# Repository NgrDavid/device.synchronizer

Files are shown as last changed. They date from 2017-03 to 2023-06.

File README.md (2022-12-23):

## Harp Synchronizer

Used to synchronize and align the different apparatus and devices present in a complex setup. It timestamps each rising or falling edge of the 9 digital input signals. The sampling of the inputs can also be configured to use a ﬁxed sampling frequency.

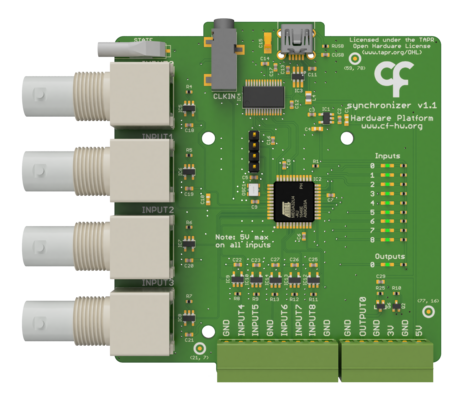
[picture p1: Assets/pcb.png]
harpsynchronizer


### Key Features ###

* Receives and timestamps up to 9 digital input signals
* Sampling on signal transitions or fixed sampling frequency up to 2kHz

### Connectivity ###

* 1x clock sync input (CLKIN) [stereo jack]
* 1x USB (for computer) [USB type B]
* 9x digital inputs (DIN0 to DIN5) [BNC], (DIN6 to DIN8) [screw terminal]
* 1x digital output (DOUT0) [screw terminal]

## Interface ##

The interface with the Harp board can be done through [Bonsai](https://bonsai-rx.org/) or a dedicated GUI (Graphical User Interface).

In order to use this GUI, there are some software that needs to be installed:

1 - Install the [drivers](https://bitbucket.org/fchampalimaud/downloads/downloads/UsbDriver-2.12.26.zip).

2 - Install the [runtime](https://bitbucket.org/fchampalimaud/downloads/downloads/Runtime-1.0.zip).

3 - Reboot the computer.

4 - Install the [GUI](https://bitbucket.org/fchampalimaud/downloads/downloads/Harp%20Synchronizer%20v1.2.0.zip).

## Licensing ##

Each subdirectory will contain a license or, possibly, a set of licenses if it involves both hardware and software.

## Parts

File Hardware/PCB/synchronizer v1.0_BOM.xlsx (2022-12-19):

Board | Part(s) | Quantity | Description | Distributor | Part. No.
 | IC1 | 1 | LDO 150mA 30V Ultra-Lo IQ Wd Input LDO Reg | Mouser | TPS70933DBVR
 | IC2 | 1 | IC MCU 8BIT 32KB FLASH 44TQFP | Mouser | 556-ATXMEGA32A4U-AU
 | IC3 | 1 | ESD Protection Low Cap | Mouser | 511-USBLC6-2SC6
 | IC4 | 1 | IC USB USB to Serial UART Enhanced IC SSOP-28 | Mouser | 895-FT232RL
 | IC5, IC6, IC7, IC8, IC9, IC10, IC12, IC13, IC14 | 9 | SingleBuffer / Driver, Inverting, 3-State, 1.65V to 5.5V, SOT-23-5 | Mouser | 595-SN74LVC1G240DBVT
 | IC11 | 1 | Buffers e line drivers 1.65-5.5V Single Non-Inverting TTL | Mouser | 863-M74VHC1GT50DTT1G
 | C12, C13 | 2 | CAP CER 47pF 50V C0G 5% 0402 | Mouser | 77-VJ0402A470JXACBC
 | CUSB | 1 | CAP CER 4.7nF 100V 10% X7R 0402 | Mouser | 81-GRM155R72A472KA01
 | C2, C5, C6, C7, C8, C11, C14, C16, C17, C18, C19, C20, C21, C22, C23, C24, C25, C26, C27 | 19 | CAP CER 100nF 10V X5R 0402 | REEL | REEL
 | C9 | 1 | CAP CER 0.33uF 10V 10% X5R 0402 | Mouser | GRM155R61A334KE15D
 | C15 | 1 | CAP TAN 4.7uF 6.3V 10% 1206 | Mouser | 80-T491A475K006
 | C4 | 1 | CAP CER 4.7uF 10V 10% X5R 0603 | Mouser | GRM188R61A475KE15D
 | C1, C10 | 2 | CAP CER 10uF 10V 10% X5R 0603 | Mouser | 81-GRM188R61A106KE9D
 | R24 | 1 | RES SMD 0Ω OHM 5% 0402 | Mouser | 71-CRCW0402-0-E3
 | R1, R14, R15, R16, R17, R18, R19, R20, R21, R22, R23 | 11 | RES SMD 68Ω OHM 5% 0402 | Mouser | 71-CRCW0402-68-E3
 | R3 | 1 | RES SMD 680Ω 0.5% 0402 | Mouser | 754-RR0510P-681D
 | R2 | 1 | RES SMD 2050Ω 1% 0402 | Mouser | 71-CRCW0402-2.05K-E3
 | R4, R5, R6, R7, R8, R9, R11, R12, R13 | 9 | RES SMD 100kΩ 1% 0402 | REEL | REEL
 | RUSB | 1 | RES SMD 1MΩ 1/4W 5% 75V 0603 | Mouser | 71-CRCW06031M00JNEAH
 | L4 | 1 | 40ohms 100MHz 1.5A Monolithic 0805 SMD | Mouser | 875-MI0805K400R-10
 | RX, STATE, OUT00, OUT01, OUT02, OUT03, OUT04, OUT05, OUT10, OUT11, OUT12, OUT13 | 12 | GREEN LED | Mouser | 78-TLMP1100-GS08
 | TX | 1 | RED LED | Mouser | 720-LSQ976-NR-1
 | OSC1 | 1 | 32MHz 10ppm | Mouser | 998-1001CI5032.0000T
 | PDI | 1 | 4POS HDR 30AU | Mouser | 649-68000-104HLF
 | A0, A1 | 2 | 3POS Gold Male | Mouser | 649-68001-203HLF
 |  | 1 | SHUNT JUMPER, 2POS | Farnell | 2396301
 | CTRL0.0, CTRL0.1, CTRL0.2, CTRL0.3, CTRL0.4, CTRL0.5 | 6 | R.A. JACK 50 OHM | Mouser | 571-5227161-1
 | X1 | 1 | TERMINAL BLOCK, HEADER, 8POS, TH | Farnell | 2517863
 |  | 1 | Pluggable Terminal Block, 8, 125 V, 12 A, 3.5 mm, 28 AWG, 16 AWG | Farnell | 2575220
 | USB | 1 | UX60-MB-5S8 | Mouser | 798-UX60-MB-5S8
 | USB Cable | 1 | USB A - MINI-B 0.8M - MINI-B 0.8M BLACK | Mouser | 538-88732-8502
 | CLKIN | 1 | SMT 3.5 STEREO REEL | Mouser | 502-35RASMT2BHNTRX
 | Standoff Top | 9 | Standoff, Nylon 6.6 (Polyamide 6.6), Hex Female, M3, 8 mm | Farnell | 1733419
 | Standoff Bottom | 9 | Standoff, Nylon 6.6 (Polyamide 6.6), Hex Male-Female, M3, 8 mm | Farnell | 1733427
 | Screws | 18 | Screw, M3, 6 mm, Nylon (Polyamide), Pan Head Slotted | Farnell | 1514409
 |  | 1 | Acrylics
 | Components | 132
 | Licensed under the TAPR Open Hardware License (www.tapr.org/OHL)
 | Copyright 2017 Artur Silva and Filipe Carvalho

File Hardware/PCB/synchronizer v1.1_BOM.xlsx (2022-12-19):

Part(s) | Quantity | Description | Distributor | Part. No.
IC1 | 1 | LDO 150mA 30V Ultra-Lo IQ Wd Input LDO Reg | Mouser | TPS70933DBVR
IC2 | 1 | IC MCU 8BIT 32KB FLASH 44TQFP | Mouser | 556-ATXMEGA32A4U-AU
IC3 | 1 | ESD Protection Low Cap | Mouser | 511-USBLC6-2SC6
IC4 | 1 | IC USB USB to Serial UART Enhanced IC SSOP-28 | Mouser | 895-FT232RL
IC5, IC6, IC7, IC8, IC9, IC10, IC12, IC13, IC14 | 9 | SingleBuffer / Driver, Inverting, 3-State, 1.65V to 5.5V, SOT-23-5 | Mouser | 595-SN74LVC1G240DBVT
C12, C13 | 2 | CAP CER 47pF 50V C0G 5% 0402 | Mouser | 77-VJ0402A470JXACBC
CUSB | 1 | CAP CER 4.7nF 100V 10% X7R 0402 | Mouser | 81-GRM155R72A472KA01
C2, C5, C6, C7, C8, C11, C14, C16, C17, C18, C19, C20, C21, C22, C23, C25, C26, C27 | 18 | CAP CER 100nF 25V X5R 0402
C3, C29 | 0 | NA | NA
C9 | 1 | CAP CER 0.33uF 10V 10% X5R 0402 | Mouser | GRM155R61A334KE15D
C15 | 1 | CAP TAN 4.7uF 6.3V 10% 1206 | Mouser | 80-T491A475K006
C4 | 1 | CAP CER 4.7uF 10V 10% X5R 0603 | Mouser | GRM188R61A475KE15D
C1, C10 | 2 | CAP CER 10uF 10V 10% X5R 0603 | Mouser | 81-GRM188R61A106KE9D
R1, R14, R15, R16, R17, R18, R19, R20, R21, R22, R23 | 11 | RES SMD 68Ω OHM 5% 0402 | Mouser | 71-CRCW0402-68-E3
R4, R5, R6, R7, R8, R9, R10, R11, R12, R13 | 10 | RES SMD 100kΩ 1% 0402
R25 | 1 | RES SMD 10kΩ 1% 0402
RUSB | 1 | RES SMD 1MΩ 1/4W 5% 75V 0603 | Mouser | 71-CRCW06031M00JNEAH
L4 | 1 | 40ohms 100MHz 1.5A Monolithic 0805 SMD | Mouser | 875-MI0805K400R-10
STATE, OUT00, OUT01, OUT02, OUT03, OUT04, OUT05, OUT10, OUT11, OUT12, OUT13 | 11 | GREEN LED | Mouser | 78-TLMP1100-GS08
Q2 | 1 |  | Farnell | 1843701
Q6 | 1 |  | Farnell | 1858672
OSC1 | 1 | 32MHz 10ppm | Mouser | 998-1001CI5032.0000T
PDI | 1 | 4POS HDR 30AU | Mouser | 649-68000-104HLF
IN0.0, IN0.1, IN0.2, IN0.3 | 4 | R.A. JACK 50 OHM | Mouser | 571-5227161-1
X1 | 1 | TERMINAL BLOCK, HEADER, 8POS, TH | Farnell | 2517863
 | 1 | Pluggable Terminal Block, 8, 125 V, 12 A, 3.5 mm, 28 AWG, 16 AWG | Farnell | 2575220
X2 | 1 | TERMINAL BLOCK, HEADER, 6POS, TH | Farnell | 2517862
 | 1 | Pluggable Terminal Block, 6, 125 V, 12 A, 3.5 mm, 28 AWG, 16 AWG | Farnell | 2575219
USB | 1 | UX60-MB-5S8 | Mouser | 798-UX60-MB-5S8
USB Cable | 1 | USB A - MINI-B 0.8M - MINI-B 0.8M BLACK | Mouser | 538-88732-8502
CLKIN | 1 | SMT 3.5 STEREO REEL | Mouser | 502-35RASMT2BHNTRX
NUT_M3_HEX_NYLON | 8 | Nut, Hex, M3, Nylon 6.6 | Farnell | 2472687
SCREW_M3_10MM_NYLON_PHILLIPS | 4 | Machine Screw, M3, 10 mm, Nylon (Polyamide), Pan Head Slotted | Farnell | 1514410
Components | 101
Licensed under the TAPR Open Hardware License (www.tapr.org/OHL)
Copyright 2017 Artur Silva and Filipe Carvalho

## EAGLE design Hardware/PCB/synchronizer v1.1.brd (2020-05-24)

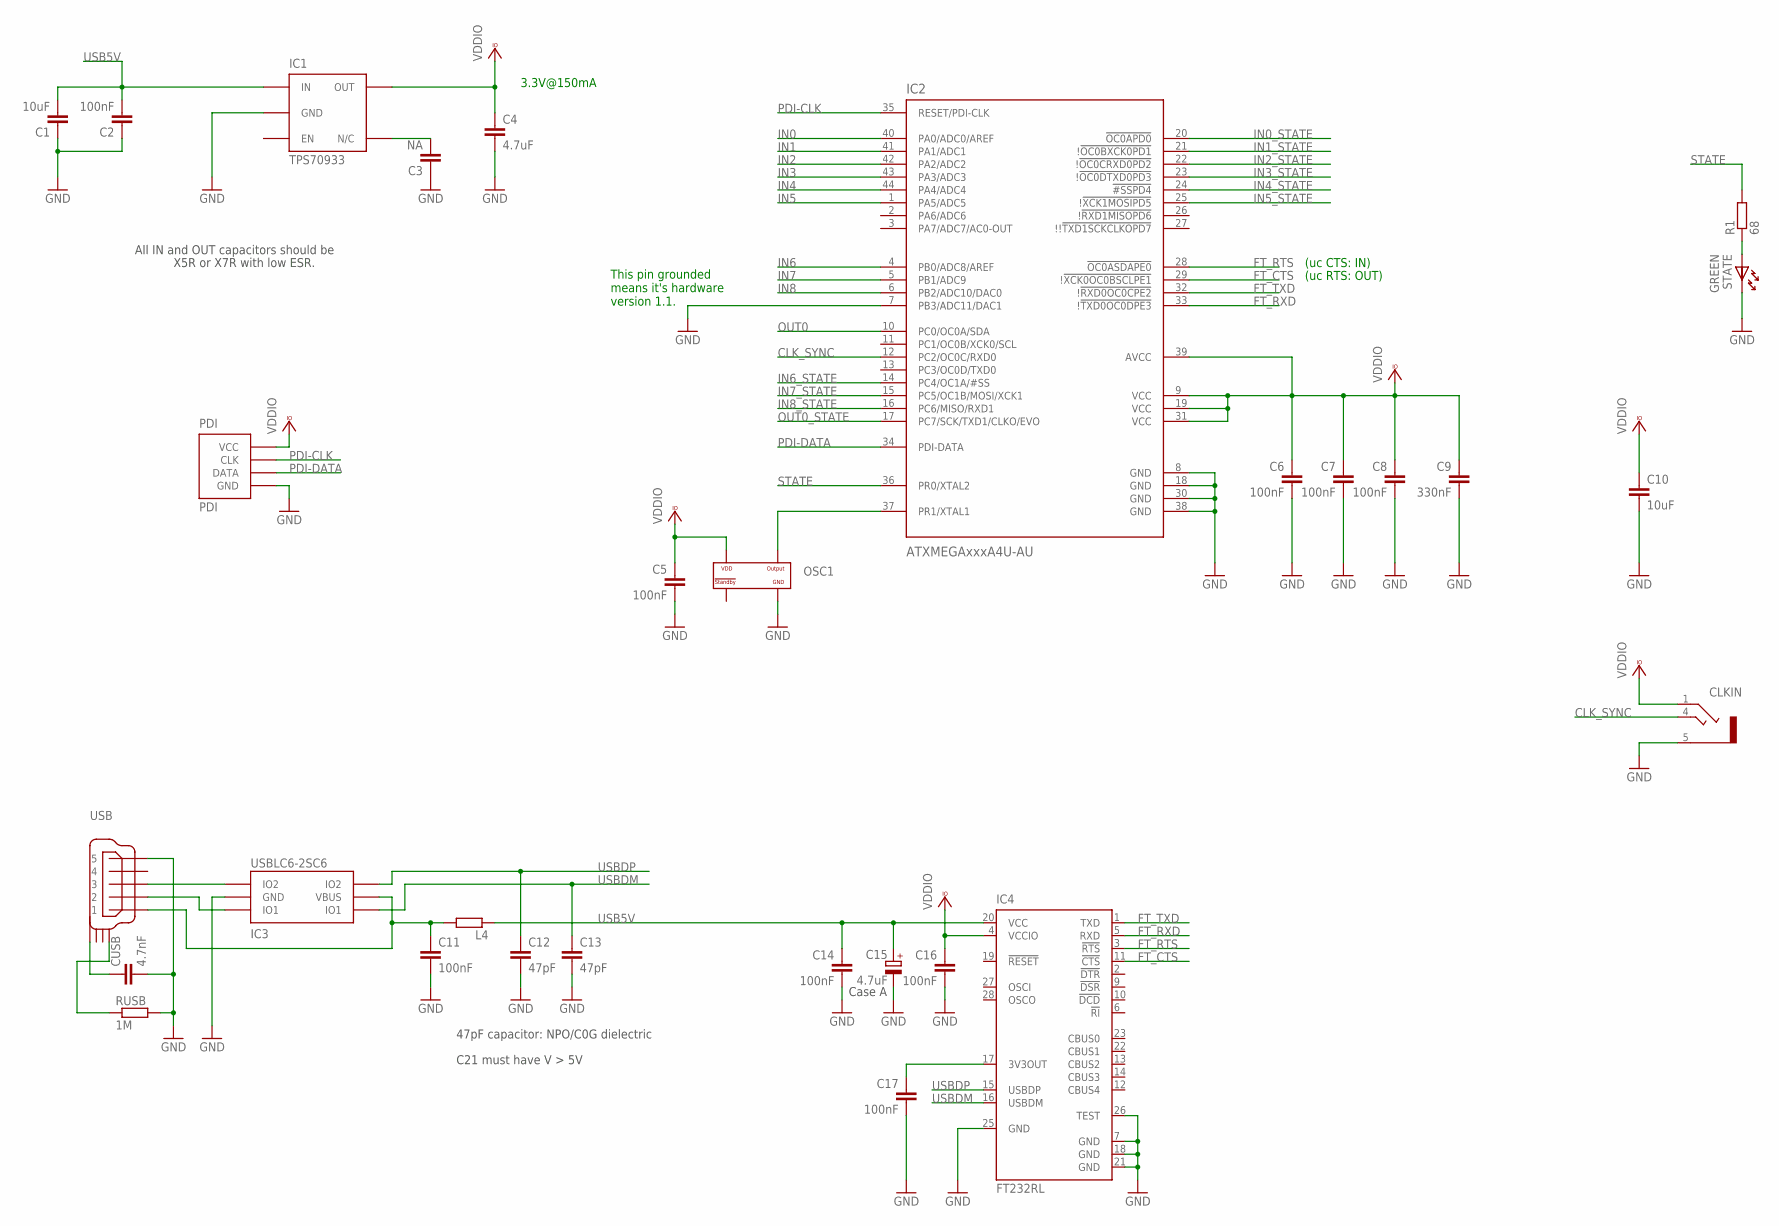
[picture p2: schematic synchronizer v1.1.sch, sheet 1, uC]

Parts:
C1, C10: 10uF; C0603
C2, C5, C6, C7, C8, C11, C14, C16, C17: 100nF; C0402
C3: NA; C0402
C4: 4.7uF; C0603
C9: 330nF; C0402
C12, C13: 47pF; C0402
C15: 4.7uF; A/3216-18W
CLKIN: STEREO_JACK; 35RASMT2BHNTRX
CUSB: 4.7nF; C0402
IC1: TPS70933; TSOT23-5
IC2: ATXMEGAxxxA4U-AU; QFP80P1200X1200X120-44N
IC3: USBLC6-2SC6; SOT23-6L
IC4: FT232RL; SSOP28
L4: ???; R0805
OSC1: OSCILLATOR; OSCILLATOR_3.2X2.5
PDI: PDI; PDI_2.54_1X4
R1: 68; R0402
RUSB: 1M; R0603
STATE: GREEN; LED_HAND
USB: USB_MINI_B; 240-0002-1

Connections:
CLK_SYNC: CLKIN.4, IC2.12 (PC2/OC0C/RXD0)
FT_CTS: IC2.29 (!!XCK0OC0BSCLPE1), IC4.11 (!CTS)
FT_RTS: IC2.28 (!OC0ASDAPE0), IC4.3 (!RTS)
FT_RXD: IC2.33 (!!TXD0OC0DPE3), IC4.5 (RXD)
FT_TXD: IC2.32 (!!RXD0OC0CPE2), IC4.1 (TXD)
GND: C1.1, C2.1, C3.1, C4.2, C5.2, C6.2, C7.2, C8.2, C9.2, C10.2, C11.2, C12.2, C13.2, C14.2, C15.-, C16.2, C17.2, CLKIN.5, CUSB.2, IC1.2 (GND), IC2.7 (PB3/ADC11/DAC1), IC2.8 (GND), IC2.18 (GND), IC2.30 (GND), IC2.38 (GND), IC3.P$2 (GND), IC4.7 (GND), IC4.18 (GND), IC4.21 (GND), IC4.25 (GND), IC4.26 (TEST), OSC1.P$2 (GND), PDI.P$1 (GND), RUSB.2, STATE.K, USB.P$5 (5); also elsewhere on the board
IN0: IC2.40 (PA0/ADC0/AREF); also elsewhere on the board
IN0_STATE: IC2.20 (!OC0APD0); also elsewhere on the board
IN1: IC2.41 (PA1/ADC1); also elsewhere on the board
IN1_STATE: IC2.21 (!!OC0BXCK0PD1); also elsewhere on the board
IN2: IC2.42 (PA2/ADC2); also elsewhere on the board
IN2_STATE: IC2.22 (!!OC0CRXD0PD2); also elsewhere on the board
IN3: IC2.43 (PA3/ADC3); also elsewhere on the board
IN3_STATE: IC2.23 (!!OC0DTXD0PD3); also elsewhere on the board
IN4: IC2.44 (PA4/ADC4); also elsewhere on the board
IN4_STATE: IC2.24 (!#SSPD4); also elsewhere on the board
IN5: IC2.1 (PA5/ADC5); also elsewhere on the board
IN5_STATE: IC2.25 (!!XCK1MOSIPD5); also elsewhere on the board
IN6: IC2.4 (PB0/ADC8/AREF); also elsewhere on the board
IN6_STATE: IC2.14 (PC4/OC1A/#SS); also elsewhere on the board
IN7: IC2.5 (PB1/ADC9); also elsewhere on the board
IN7_STATE: IC2.15 (PC5/OC1B/MOSI/XCK1); also elsewhere on the board
IN8: IC2.6 (PB2/ADC10/DAC0); also elsewhere on the board
IN8_STATE: IC2.16 (PC6/MISO/RXD1); also elsewhere on the board
unnamed: R1.1, STATE.A
unnamed: C3.2, IC1.4 (N/C)
unnamed: C17.1, IC4.17 (3V3OUT)
unnamed: C11.1, IC3.P$5 (VBUS), L4.2, USB.P$1 (1)
unnamed: IC3.P$1 (IO1), USB.P$2 (2)
unnamed: IC3.P$3 (IO2), USB.P$3 (3)
unnamed: CUSB.1, USB.SHIELD_4
unnamed: RUSB.1, USB.SHIELD_1
OSC1: IC2.37 (PR1/XTAL1), OSC1.P$3 (OUTPUT)
OUT0: IC2.10 (PC0/OC0A/SDA); also elsewhere on the board
OUT0_STATE: IC2.17 (PC7/SCK/TXD1/CLKO/EVO); also elsewhere on the board
PDI-CLK: IC2.35 (RESET/PDI-CLK), PDI.P$3 (CLK)
PDI-DATA: IC2.34 (PDI-DATA), PDI.P$2 (DATA)
STATE: IC2.36 (PR0/XTAL2), R1.2
USB5V: C1.2, C2.2, C14.1, C15.+, IC1.1 (IN), IC4.20 (VCC), L4.1; also elsewhere on the board
USBDM: C13.1, IC3.P$6 (IO1), IC4.16 (USBDM)
USBDP: C12.1, IC3.P$4 (IO2), IC4.15 (USBDP)
VCCIO: C4.1, C5.1, C6.1, C7.1, C8.1, C9.1, C10.1, C16.1, CLKIN.1, IC1.5 (OUT), IC2.9 (VCC), IC2.19 (VCC), IC2.31 (VCC), IC2.39 (AVCC), IC4.4 (VCCIO), OSC1.P$4 (VDD), PDI.P$4 (VCC); also elsewhere on the board

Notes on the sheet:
Case A
47pF capacitor: NPO/C0G dielectric
C21 must have V > 5V
(uc CTS: IN)
(uc RTS: OUT)
This pin grounded means it's hardware version 1.1.
All IN and OUT capacitors should be
X5R or X7R with low ESR.
3.3V@150mA

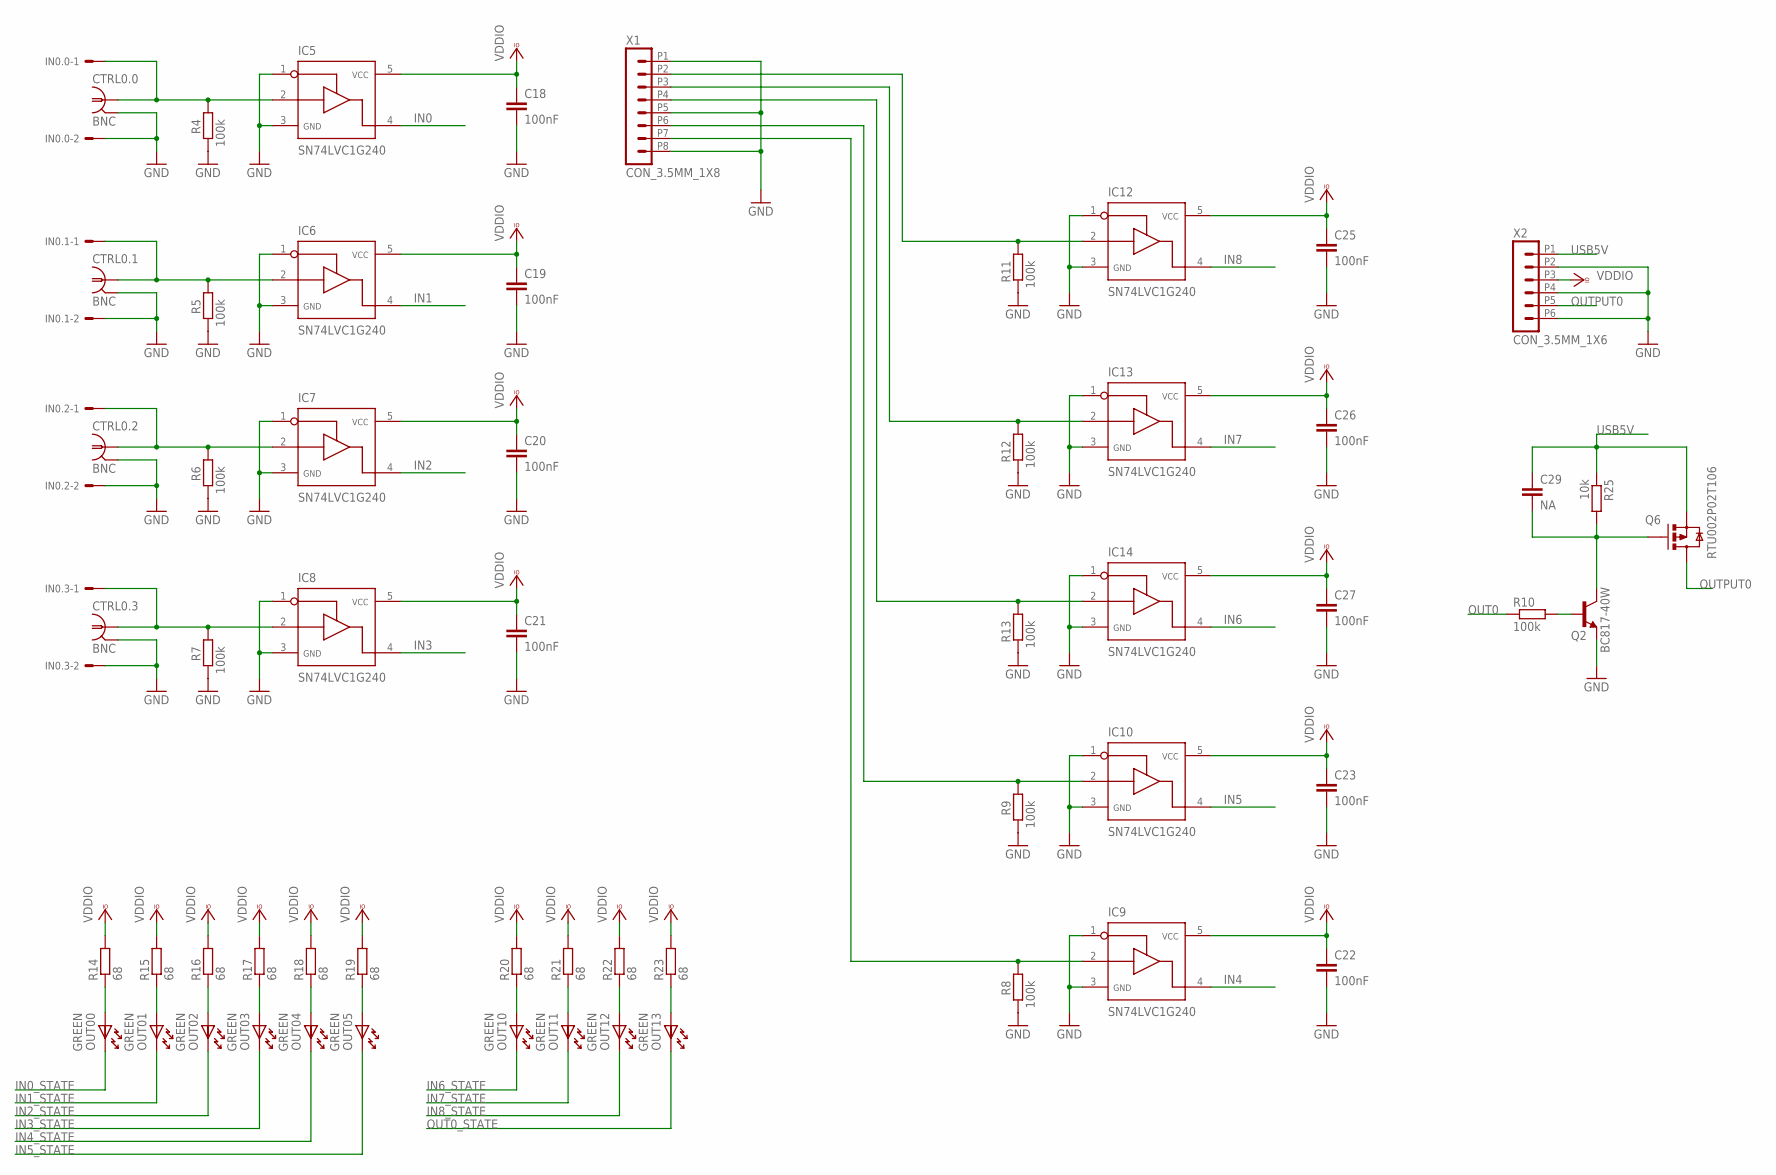
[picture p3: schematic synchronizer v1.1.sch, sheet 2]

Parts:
C18, C19, C20, C21, C22, C23, C25, C26, C27: 100nF; C0402
C29: NA; C0402
CTRL0.0, CTRL0.1, CTRL0.2, CTRL0.3: BNC; BNC_RA
IC5, IC6, IC7, IC8, IC9, IC10, IC12, IC13, IC14: SN74LVC1G240; SOT23-5
IN0.0, IN0.1, IN0.2, IN0.3: 22-05-7028-02; 7395-02
OUT00, OUT01, OUT02, OUT03, OUT04, OUT05, OUT10, OUT11, OUT12, OUT13: GREEN; LED_HAND
Q2: BC817-40W; SOT323-BEC
Q6: RTU002P02T106; SOT323
R4, R5, R6, R7, R8, R9, R10, R11, R12, R13: 100k; R0402
R14, R15, R16, R17, R18, R19, R20, R21, R22, R23: 68; R0402
R25: 10k; R0402
X1: CON_3.5MM_1X8
X2: CON_3.5MM_1X6

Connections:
GND: C18.2, C19.2, C20.2, C21.2, C22.2, C23.2, C25.2, C26.2, C27.2, CTRL0.0.2, CTRL0.1.2, CTRL0.2.2, CTRL0.3.2, IC5.1, IC5.3, IC6.1, IC6.3, IC7.1, IC7.3, IC8.1, IC8.3, IC9.1, IC9.3, IC10.1, IC10.3, IC12.1, IC12.3, IC13.1, IC13.3, IC14.1, IC14.3, IN0.0.2, IN0.1.2, IN0.2.2, IN0.3.2, Q2.E, R4.2, R5.2, R6.2, R7.2, R8.2, R9.2, R11.2, R12.2, R13.2, X1.P1 (1), X1.P5 (5), X1.P8 (8), X2.P2 (2), X2.P4 (4), X2.P6 (6); also elsewhere on the board
IN0: IC5.4; also elsewhere on the board
IN0_STATE: OUT00.K; also elsewhere on the board
IN1: IC6.4; also elsewhere on the board
IN1_STATE: OUT01.K; also elsewhere on the board
IN2: IC7.4; also elsewhere on the board
IN2_STATE: OUT02.K; also elsewhere on the board
IN3: IC8.4; also elsewhere on the board
IN3_STATE: OUT03.K; also elsewhere on the board
IN4: IC9.4; also elsewhere on the board
IN4_STATE: OUT04.K; also elsewhere on the board
IN5: IC10.4; also elsewhere on the board
IN5_STATE: OUT05.K; also elsewhere on the board
IN6: IC14.4; also elsewhere on the board
IN6_STATE: OUT10.K; also elsewhere on the board
IN7: IC13.4; also elsewhere on the board
IN7_STATE: OUT11.K; also elsewhere on the board
IN8: IC12.4; also elsewhere on the board
IN8_STATE: OUT12.K; also elsewhere on the board
unnamed: CTRL0.1.1, IC6.2, IN0.1.1, R5.1
unnamed: CTRL0.2.1, IC7.2, IN0.2.1, R6.1
unnamed: CTRL0.3.1, IC8.2, IN0.3.1, R7.1
unnamed: IC12.2, R11.1, X1.P2 (2)
unnamed: IC13.2, R12.1, X1.P3 (3)
unnamed: IC14.2, R13.1, X1.P4 (4)
unnamed: OUT00.A, R14.1
unnamed: OUT01.A, R15.1
unnamed: OUT02.A, R16.1
unnamed: OUT03.A, R17.1
unnamed: OUT04.A, R18.1
unnamed: OUT05.A, R19.1
unnamed: OUT10.A, R20.1
unnamed: OUT11.A, R21.1
unnamed: OUT12.A, R22.1
unnamed: OUT13.A, R23.1
unnamed: IC9.2, R8.1, X1.P7 (7)
unnamed: IC10.2, R9.1, X1.P6 (6)
unnamed: CTRL0.0.1, IC5.2, IN0.0.1, R4.1
unnamed: C29.2, Q2.C, Q6.2 (G), R25.2
unnamed: Q2.B, R10.2
OUT0: R10.1; also elsewhere on the board
OUT0_STATE: OUT13.K; also elsewhere on the board
OUTPUT0: Q6.3 (D), X2.P5 (5)
USB5V: C29.1, Q6.1 (S), R25.1, X2.P1 (1); also elsewhere on the board
VCCIO: C18.1, C19.1, C20.1, C21.1, C22.1, C23.1, C25.1, C26.1, C27.1, IC5.5, IC6.5, IC7.5, IC8.5, IC9.5, IC10.5, IC12.5, IC13.5, IC14.5, R14.2, R15.2, R16.2, R17.2, R18.2, R19.2, R20.2, R21.2, R22.2, R23.2, X2.P3 (3); also elsewhere on the board

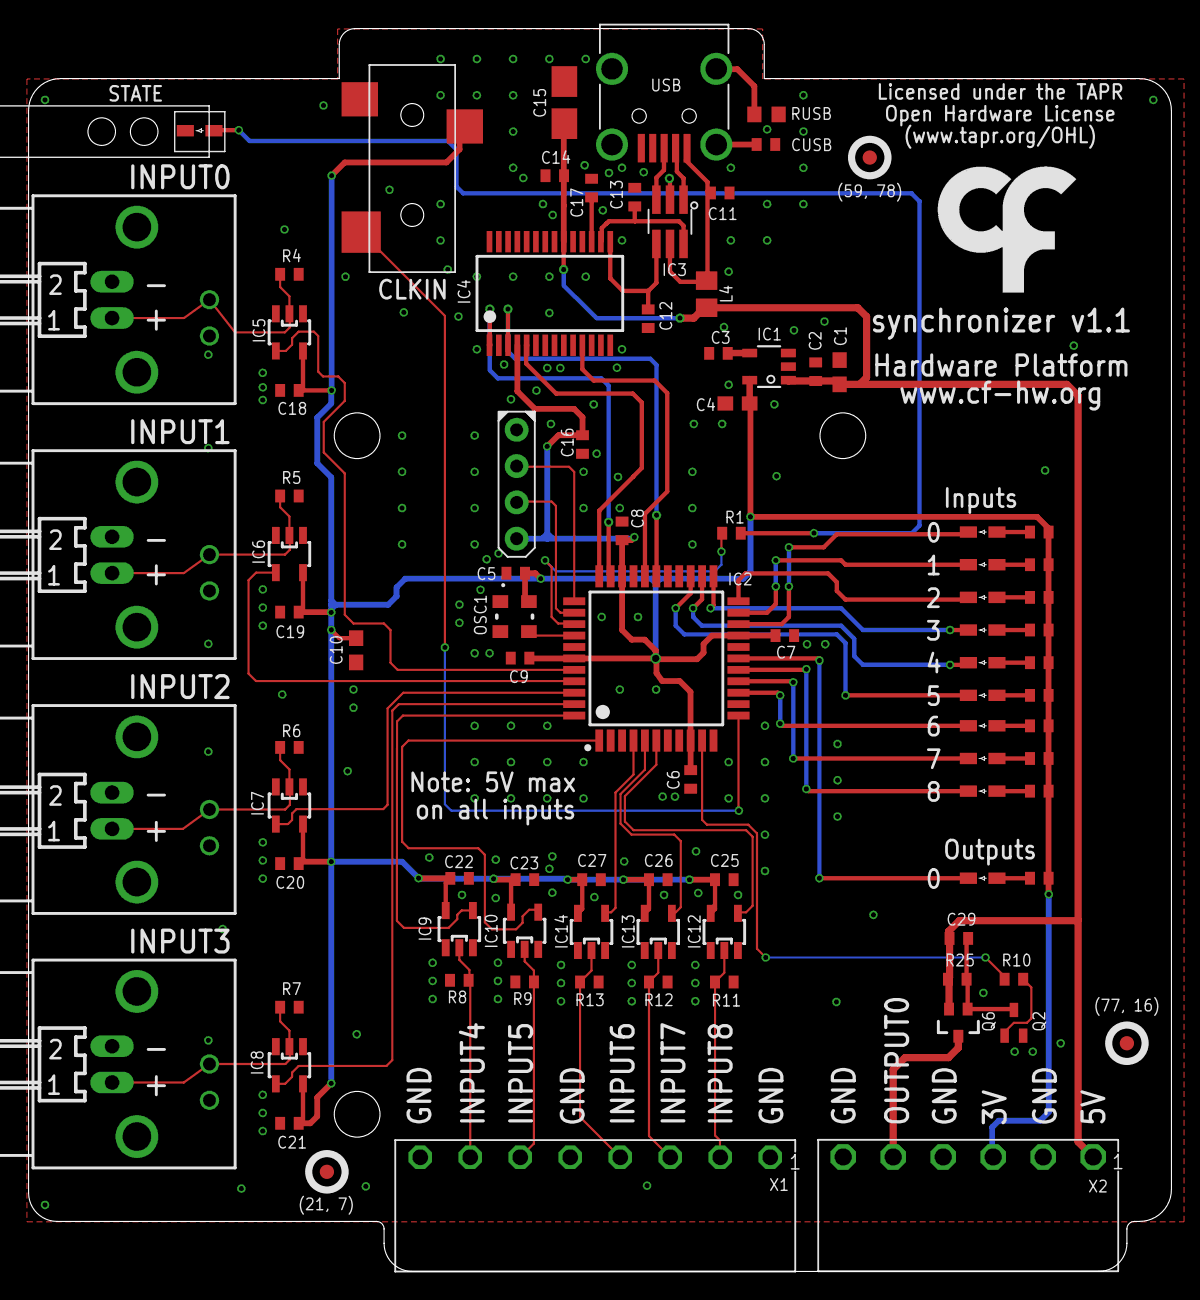
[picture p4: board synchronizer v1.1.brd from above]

Board: 2 copper layers, 80.0 x 87.0 mm, 97 parts (0 on the bottom side), 64 nets.

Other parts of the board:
U$1: LED_PIPE_7513D2-L
U$2, U$3, U$7: FIDUCIAL
U$9: LOGO_6

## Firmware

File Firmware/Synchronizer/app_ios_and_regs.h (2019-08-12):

#ifndef _APP_IOS_AND_REGS_H_
#define _APP_IOS_AND_REGS_H_
#include "cpu.h"

void init_ios(void);
/************************************************************************/
/* Definition of input pins                                             */
/************************************************************************/
// INPUT0                 Description: Input 0
// INPUT1                 Description: Input 1
// INPUT2                 Description: Input 2
// INPUT3                 Description: Input 3
// INPUT4                 Description: Input 4
// INPUT5                 Description: Input 5
// INPUT6                 Description: Input 6
// INPUT7                 Description: Input 7
// INPUT8                 Description: Input 8
// ADD0                   Description: Adress 0
// ADD1                   Description: Adress 1

#define read_INPUT0 read_io(PORTA, 0)           // INPUT0
#define read_INPUT1 read_io(PORTA, 1)           // INPUT1
#define read_INPUT2 read_io(PORTA, 2)           // INPUT2
#define read_INPUT3 read_io(PORTA, 3)           // INPUT3
#define read_INPUT4 read_io(PORTA, 4)           // INPUT4
#define read_INPUT5 read_io(PORTA, 5)           // INPUT5
#define read_INPUT6 read_io(PORTB, 0)           // INPUT6
#define read_INPUT7 read_io(PORTB, 1)           // INPUT7
#define read_INPUT8 read_io(PORTB, 2)           // INPUT8
#define read_ADD0 read_io(PORTA, 7)             // ADD0
#define read_ADD1 read_io(PORTC, 1)             // ADD1

/************************************************************************/
/* Definition of output pins                                            */
/************************************************************************/
// LEDIN0                 Description: Board's LED for Input 0
// LEDIN1                 Description: Board's LED for Input 1
// LEDIN2                 Description: Board's LED for Input 2
// LEDIN3                 Description: Board's LED for Input 3
// LEDIN4                 Description: Board's LED for Input 4
// LEDIN5                 Description: Board's LED for Input 5
// LEDIN6                 Description: Board's LED for Input 6
// LEDIN7                 Description: Board's LED for Input 7
// LEDIN8                 Description: Board's LED for Input 8
// LEDOUT0                Description: Board's LED for Output 0
// OUTPUT0                Description: Output 0

/* LEDIN0 */
#define set_LEDIN0 clear_io(PORTD, 0)
#define clr_LEDIN0 set_io(PORTD, 0)
#define tgl_LEDIN0 toggle_io(PORTD, 0)
#define read_LEDIN0 read_io(PORTD, 0)

/* LEDIN1 */
#define set_LEDIN1 clear_io(PORTD, 1)
#define clr_LEDIN1 set_io(PORTD, 1)
#define tgl_LEDIN1 toggle_io(PORTD, 1)
#define read_LEDIN1 read_io(PORTD, 1)

/* LEDIN2 */
#define set_LEDIN2 clear_io(PORTD, 2)
#define clr_LEDIN2 set_io(PORTD, 2)
#define tgl_LEDIN2 toggle_io(PORTD, 2)
#define read_LEDIN2 read_io(PORTD, 2)

/* LEDIN3 */
#define set_LEDIN3 clear_io(PORTD, 3)
#define clr_LEDIN3 set_io(PORTD, 3)
#define tgl_LEDIN3 toggle_io(PORTD, 3)
#define read_LEDIN3 read_io(PORTD, 3)

/* LEDIN4 */
#define set_LEDIN4 clear_io(PORTD, 4)
#define clr_LEDIN4 set_io(PORTD, 4)
#define tgl_LEDIN4 toggle_io(PORTD, 4)
#define read_LEDIN4 read_io(PORTD, 4)

/* LEDIN5 */
#define set_LEDIN5 clear_io(PORTD, 5)
#define clr_LEDIN5 set_io(PORTD, 5)
#define tgl_LEDIN5 toggle_io(PORTD, 5)
#define read_LEDIN5 read_io(PORTD, 5)

/* LEDIN6 */
#define set_LEDIN6 clear_io(PORTC, 4)
#define clr_LEDIN6 set_io(PORTC, 4)
#define tgl_LEDIN6 toggle_io(PORTC, 4)
#define read_LEDIN6 read_io(PORTC, 4)

/* LEDIN7 */
#define set_LEDIN7 clear_io(PORTC, 5)
#define clr_LEDIN7 set_io(PORTC, 5)
#define tgl_LEDIN7 toggle_io(PORTC, 5)
#define read_LEDIN7 read_io(PORTC, 5)

/* LEDIN8 */
#define set_LEDIN8 clear_io(PORTC, 6)
#define clr_LEDIN8 set_io(PORTC, 6)
#define tgl_LEDIN8 toggle_io(PORTC, 6)
#define read_LEDIN8 read_io(PORTC, 6)

/* LEDOUT0 */
#define set_LEDOUT0 clear_io(PORTC, 7)
#define clr_LEDOUT0 set_io(PORTC, 7)
#define tgl_LEDOUT0 toggle_io(PORTC, 7)
#define read_LEDOUT0 read_io(PORTC, 7)

/* OUTPUT0 */
#define set_OUTPUT0 set_io(PORTC, 0)
#define clr_OUTPUT0 clear_io(PORTC, 0)
#define tgl_OUTPUT0 toggle_io(PORTC, 0)
#define read_OUTPUT0 read_io(PORTC, 0)


/************************************************************************/
/* Registers' structure                                                 */
/************************************************************************/
typedef struct
{
	uint16_t REG_INPUTS_STATE;
	uint8_t REG_OUTPUTS;
	uint8_t REG_INPUT_CATCH_MODE;
	uint8_t REG_OUTPUT_MODE;
	uint8_t REG_RESERVED0;
	uint8_t REG_RESERVED1;
	uint8_t REG_RESERVED2;
	uint8_t REG_RESERVED3;
	uint8_t REG_EVNT_ENABLE;
} AppRegs;

/************************************************************************/
/* Registers' address                                                   */
/************************************************************************/
/* Registers */
#define ADD_REG_INPUTS_STATE                32 // U16    State of each input (the address is included in the MSbits)
#define ADD_REG_OUTPUTS                     33 // U8     
#define ADD_REG_INPUT_CATCH_MODE            34 // U8     Configures when inputs will be catched
#define ADD_REG_OUTPUT_MODE                 35 // U8     Configures how the output behaves
#define ADD_REG_RESERVED0                   36 // U8     Not used
#define ADD_REG_RESERVED1                   37 // U8     Not used
#define ADD_REG_RESERVED2                   38 // U8     Not used
#define ADD_REG_RESERVED3                   39 // U8     Not used
#define ADD_REG_EVNT_ENABLE                 40 // U8     Enable the Events

/************************************************************************/
/* PWM Generator registers' memory limits                               */
/*                                                                      */
/* DON'T change the APP_REGS_ADD_MIN value !!!                          */
/* DON'T change these names !!!                                         */
/************************************************************************/
/* Memory limits */
#define APP_REGS_ADD_MIN                    0x20
#define APP_REGS_ADD_MAX                    0x28
#define APP_NBYTES_OF_REG_BANK              10

/************************************************************************/
/* Registers' bits                                                      */
/************************************************************************/
#define MSK_ADDRESS                        (3<<14)      // Board's address
#define MSK_INPUTS                         (0x1FF<<0)   // Board's inputs
#define B_INPUT0                           (1<<0)       // Input 0
#define B_INPUT1                           (1<<1)       // Input 1
#define B_INPUT2                           (1<<2)       // Input 2
#define B_INPUT3                           (1<<3)       // Input 3
#define B_INPUT4                           (1<<4)       // Input 4
#define B_INPUT5                           (1<<5)       // Input 5
#define B_INPUT6                           (1<<6)       // Input 6
#define B_INPUT7                           (1<<7)       // Input 7
#define B_INPUT8                           (1<<8)       // Input 8
#define B_OUTPUT0_STATE                    (1<<13)      // Reflects the Output 0 state
#define B_ADRESS0                          (1<<14)      // Address 0
#define B_ADRESS1                          (1<<15)      // Address 1
#define B_OUTPUT0                          (1<<0)       // Output 0
#define MSK_CATCH_MODE                     (15<<0)      // Catch mode
#define GM_INMODE_DISABLED                 (0<<0)       // Catch is disabled
#define GM_INMODE_WHEN_ANY_CHANGE          (1<<0)       // Catched everytime one of the Inputs changes
#define GM_INMODE_RISE_ON_INPUT0           (2<<0)       // Catched when Input 0 have a rising edge
#define GM_INMODE_FALL_ON_INPUT0           (3<<0)       // Catched when Input 0 have a falling edge
#define GM_INMODE_100Hz                    (4<<0)       // Catched at a frequency of 100 Hz
#define GM_INMODE_250Hz                    (5<<0)       // Catched at a frequency of 250 Hz
#define GM_INMODE_500Hz                    (6<<0)       // Catched at a frequency of 500 Hz
#define GM_INMODE_1000Hz                   (7<<0)       // Catched at a frequency of 1 KHz
#define GM_INMODE_2000Hz                   (8<<0)       // Catched at a frequency of 2 KHz
#define MSK_OUTPUT_MODE                    (15<<0)      // Output mode
#define GM_OUTMODE_NOT_USED                (0<<0)       // Not used by the catch
#define GM_OUTMODE_TOGGLE                  (1<<0)       // Output toggles everytime the inputs are catched
#define GM_OUTMODE_INPUT0                  (2<<0)       // Output is equal to Input 0 (bit INPUT0)
#define GM_OUTMODE_PULSE_5mS               (3<<0)       // Output has a positive pulse of 5 milliseconds everytime the inputs are catched
#define GM_OUTMODE_PULSE_2mS               (4<<0)       // Output has a positive pulse of 2 milliseconds everytime the inputs are catched
#define GM_OUTMODE_PULSE_1mS               (5<<0)       // Output has a positive pulse of 1 milliseconds everytime the inputs are catched
#define GM_OUTMODE_PULSE_500uS             (6<<0)       // Output has a positive pulse of 500 microseconds everytime the inputs are catched
#define GM_OUTMODE_PULSE_250uS             (7<<0)       // Output has a positive pulse of 250 microseconds everytime the inputs are catched
#define GM_OUTMODE_OR                      (8<<0)       // Logic OR of all the inputs
#define B_EVT0                             (1<<0)       // Event of register INPUTS_STATE

#endif /* _APP_REGS_H_ */

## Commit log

2017-03-27 Added Firmware code.
    [registers.xls]
2017-03-27 Added the acrylic case.
2017-03-31 Added the PCB files.
    [synchronizer v1.0 BOM.xlsx, synchronizer v1.0.brd, synchronizer v1.0.sch]
2017-03-31 Updated BOM.
    [synchronizer v1.0 BOM.xlsx]
2017-04-04 Updated registers.xls.
    [registers.xls]
2017-04-27 Corrected some bit positions.
    [registers.xls]
2018-01-25 Updated to Harp 1.2.
    [registers.xls]
2018-03-05 Fixed an issue that was preventing the correct input state indication on the Leds.
2019-08-12 Added new feature (output 0 as a logic OR of all inputs) and updated firmware version to 1.5.
    [registers.xls]
2020-05-24 Added fabrication files.
    [synchronizer v1.1 BOM.xlsx, synchronizer v1.1 BOM_simplified.xlsx, synchronizer v1.1.brd, synchronizer v1.1.csv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]
2022-12-19 Dele case files
2022-12-19 Correct BOM files
    [synchronizer v1.0 BOM.xlsx, synchronizer v1.0_BOM.xlsx, synchronizer v1.1 BOM.xlsx, synchronizer v1.1.csv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]
2022-12-23 refactor repository structure
    [synchronizer v1.0.brd, synchronizer v1.0.sch, synchronizer v1.0_BOM.xlsx, synchronizer v1.1.brd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]
2023-06-28 update pcb asset image
2023-07-27 Edit for consistency with InputExpander board
2024-11-10 Update device schema source

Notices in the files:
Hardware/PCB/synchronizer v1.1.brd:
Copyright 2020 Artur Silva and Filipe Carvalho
